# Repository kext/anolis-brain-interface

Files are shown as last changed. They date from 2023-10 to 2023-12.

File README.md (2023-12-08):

# Anolis Brain Interface

This repository contains the hardware and software files for the Anolis Brain Interface.

## PCB

The source and production files for the flexible PCB are in the [`pcb`](pcb) directory.
See the [Readme there](pcb/README.md) for instructions to setup your work environment.

## Firmware

The firmware for the brain interface and the dongle is in the [`firmware`](firmware) directory.
There you can find more information how to compile, flash and run the firmware on your device.

## Licence

The source code and PCB design files are dual licenced under the [MIT](LICENCE-MIT) and [Apache 2.0](LICENCE-APACHE) licences.

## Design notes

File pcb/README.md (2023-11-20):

# Anolis Brain Interface PCB

## Setup

To work on the project files you need the KiCad EDA software in version 7.

KiCad can be downloaded from the [KiCad website](https://www.kicad.org/).
Download the version for your operating system and follow the instructions.

## Releases

Released versions can be found in the [`releases`](releases) directory.

## Changelog

All notable changes to the PCB should be listed below.

### [0.1.0] - 2023-11-20
- First version

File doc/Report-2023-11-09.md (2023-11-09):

2023-11-09

# Anolis Brain Interface Report

## Concept

The Anolis Brain Interface consists of a flexible PCB to be mounted on the back of a lizard of the species *Anolis carolinensis*.
It measures brain activity of the animal and transmits the data in real time to a connected PC via Bluetooth.

## What has been done so far

### PCB

We have created a draft for a PCB for use with LiPo batteries.
It features a segmented design for increased flexibility.
It is still a bit big however.

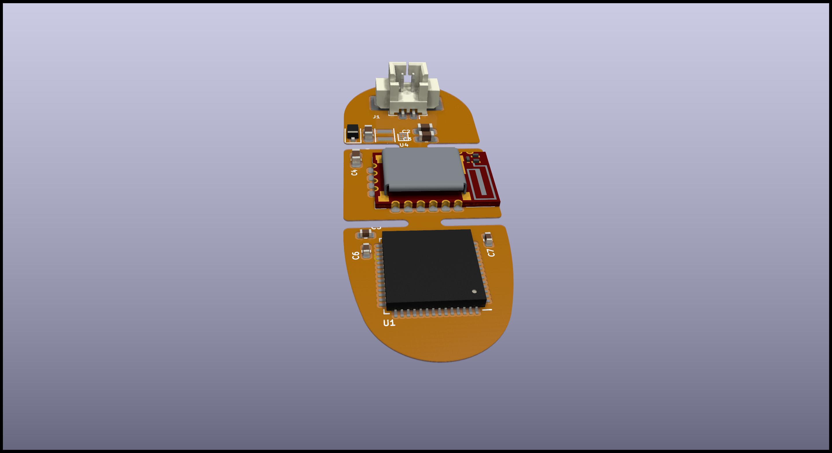
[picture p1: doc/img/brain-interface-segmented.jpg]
Segmented PCB

*Segmented PCB Draft*

After better estimation of the power requirements we will most likely change the design to use coin cell batteries instead.

We might also get rid of the segments to reduce the size further.

The brain interface is equipped with an analogue frontend in form of the Intan RHD2216 electrophysiological amplifier.
It also features the Würth Electronic Setebos-I Bluetooth module.
It contains a Bluetooth antenna and circuitry as well as the Nordic Semiconductor nRF52840 SoC which consists of a Bluetooth radio module and an ARM Cortex-M4F processor with 64MHz, 1MB flash memory and 256kB RAM.

### Software

A prototype of the software is complete by now.
It consists of three different parts.

The main software runs on the brain interface PCB.
It measures the electrophysiological signals with the Intan RHD2216 chip via SPI.
Then the collected data is transmitted in real time via a Bluetooth connection to a USB dongle.

The USB dongle runs a firmware which scans for and connects to the brain interface.
After a successful connection has been established it receives the data and transfers it via USB to the PC.

On the PC runs a frontend software in a web browser that connects to the dongle using the WebUSB API.
It collects the data and displays it in real time in the browser window.
It also saves the data for later conversion and analysis.

The software on the brain interface and the dongle are developed in the Rust language using the open-source Embassy framework.
The Embassy framework offers a high level abstraction over all the functionality of the nRF52840 SoC and makes it easy to implement concurrent tasks like reading the data from the analogue-to-digital converter while simultaneously sending data over the Bluetooth radio.

The frontend is written in Javascript using the Vue.js framework for the graphical user interface.

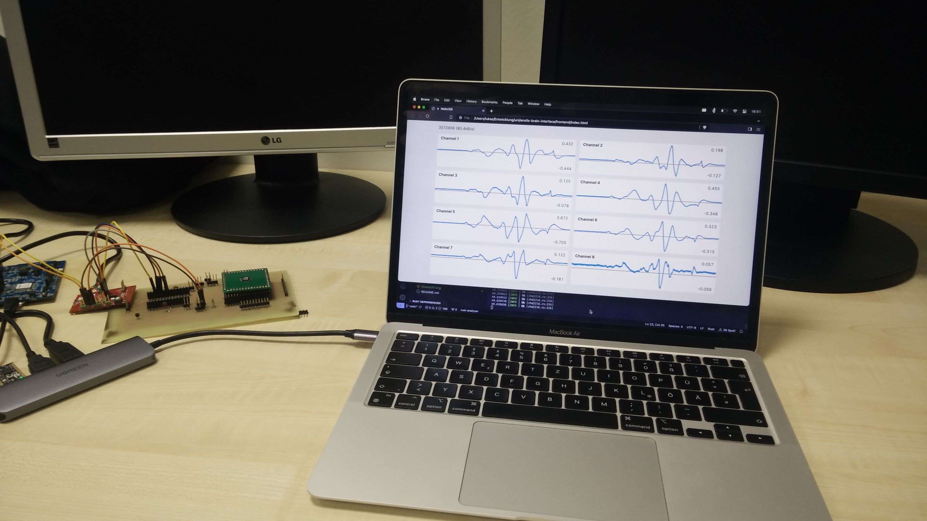
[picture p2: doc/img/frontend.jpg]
Frontend running on a laptop

*Frontend running on a laptop*

During development small improvements to the Embassy framework have been found and sent to the Embassy maintainers.
Those fixes are now upstreamed in the open-source project for the benefit of the community.

## Next steps

The biggest remaining challenge is the power supply for the system.
In the following days we will make several measurements of the power consumption of the brain interface and investigate how the sample rate and also the radio transmit power influence the power consumption.

Depending on the results of the power study we will finalize the PCB design for either a coin cell battery or a LiPo battery.
We will choose the lightest battery system that is still able to power the brain interface.

After that the software will be finalized, fixing eventual bugs and doing more testing.

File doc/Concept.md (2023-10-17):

# Concept

This project aims to build a device that is able to measure the bioelectric potential in the brains of Anolis lizards.
The device should be attached to the lizard and impact it as little as possible.

The data should be sampled at a decently high rate on multiple channels and then both be saved for later analysis and also displayed in realtime.

The realtime display is achieved by sending the data via Bluetooth to a connected PC.
Depending on the sample rate and the number of channels this is either all of the data or a reduced form.

In case only a reduced form can be sent in realtime, the data storage has to happen on the device itself.
A micro SD card would be the obvious choice for that.
Otherwise the data can just be recorded on the PC.

## Components

### Analogue Frontend

The analogue frontend is implemented with the Intan RHD2216 ADC.
It has 16 analogue differential inputs and an SPI connection to retrieve the data.

Depending on the configuration the RHD2216 draws between about 1mA to 15mA from a 3.3V power supply.

### Bluetooth Interface

The Bluetooth connectivity will be realized with the nRF52840 SoC by Nordic Semiconductor.
The SoC is powered by a 64MHz Arm Cortex M4F processor, which will not only handle the Bluetooth connection but will also run all the application code.

The highest contributor to power consumption is the Bluetooth radio.
Depending on the usage pattern the whole module should draw no more than about 20mA from the 3.3V supply while continuously transmitting data.

One of the smallest modules containing the nRF52840 is the Setebos-I by Würth Electronic.
It already contains the antenna circuit and the CPU.

For programming, a development kit with an SWD debugger is needed to flash the program onto the SoC.
The obvious choice here is the nRF52840-DK by Nordic Semiconductor.

To connect the module to a PC a Bluetooth dongle is needed.
A good choice will most likely be the nRF52840-Dongle by Nordic Semiconductor.
It uses the same nRF52840 SoC and thus supports the same level of Bluetooth communication including the new 2M PHY for higher data rate introduced in Bluetooth version 5.

### Data Storage

Data storage will happen on a micro SD card if the data rate is too high for realtime transmission.
In addition to the faster SD mode it can also be used via SPI which allows it to be connected directly to the processor.

If a micro SD card is required it will be the biggest consumer of power with peaks in excess of 100mA.
The power supply must therefore be able to handle this current and should be able to supply at least 300mA to leave enough capacity for the other components.

The micro SD card needs to be inserted into a socket.
The socket should be as small as possible and use up as little space on the board as possible.
A good choice will be the Molex socket 47571-0001.
It leaves enough clearance under the card that it can overlap other components.

### Power Supply

The system must be powered by batteries to enable a wireless operation.
Popular choices here are either rechargeable LiPo batteries often found in small model toys or Zinc-Air primary cells which have among the highest energy densities by both mass and weight, often found in hearing aids.

When using LiPo batteries, a charging circuit and voltage converter is required to keep the voltage at a steady 3.3V and to charge the battery.

For use with Zinc-Air coin cells a boost converter is needed to step up the 1.45V up to the required 3.3V.
A good choice might be the TPS610994 by Texas Instruments.
It has a very low quiescent current and can use the battery until it has dropped to 0.7V.
An even better choice might be the TPS61299 but it is not widely available yet.

## Requirements

A number of requirements have to be specified to properly dimension the project.

### Channel Count

The channel count not only influences the data rate but also dictates how much board space is needed for the connectors and the electrodes.
The maximum channel count possible with the RHD2216 is 16 channels.

Also important is if the channels should share a common reference or if each channel is using the full differential input.

### Sample Rate

The sample rate has the biggest influence on the overall data rate.
If the data rate is too high the micro SD card for data storage can not be omitted from the system.
If it is lower the complete data can be transferred via Bluetooth to be recorded directly on the PC.

### Bit Depth

The RHD2216 by default has a bit depth of 16 bits per sample.
This has a lower overall impact, but reducing the bit depth by either limiting the input range by removing high order bits or by reducing the resolution by removing low order bits can significantly decrease the data rate.
Another possibility would be using dynamic range compression, i.e. companding the signal by applying a non-linear function before reduction.

### Operating Time

The required operating time dictates how many batteries are required and how big those have to be.
A longer operating time means bigger or more batteries and thus heavier weight and larger dimensions of the overall system.

### Electrodes

The type, shape, number and dimensions of the electrodes must be known.
The electrodes influence significantly how the system has to be designed and mounted.
Possible configurations include mounting the PCB either on the head or on the back of the lizard.

## Part List

The following parts are needed for the development.

Part               | Supplier | Order Number
-------------------|----------|---------------------
nRF52840-DK        | Mouser   | [949-NRF52840-DK](https://www.mouser.de/c/?q=949-NRF52840-DK)
nRF52840-Dongle    | Mouser   | [949-NRF52840-DONGLE](https://www.mouser.de/c/?q=949-NRF52840-DONGLE)
Setebos-I          | Farnell  | [3868806](https://de.farnell.com/search?st=3868806)
TPS610994YFFR      | Mouser   | [595-TPS610994YFFR](https://www.mouser.de/c/?q=595-TPS610994YFFR)
VLS201610CX-2R2M-1 | Mouser   | [810-VLS201610CX2R2M1](https://www.mouser.de/c/?q=810-VLS201610CX2R2M1)
47571-0001         | Mouser   | [538-47571-0001](https://www.mouser.de/c/?q=538-47571-0001)

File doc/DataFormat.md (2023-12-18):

# Storage Data Format

The data file contains all data packets received by the brain interface together with the time the packet was received.
The data file includes all the data packets with a header one after the other.

Each stored packet has the following format:

Field | Byte Offset | Byte Size | Data Type | Description
------|-------------|-----------|-----------|------------
Signature | 0 | 4 | `u32` | The fixed value 0x55daba to identify the file.
Length | 4 | 4 | `u32` | Length of the stored packet in bytes including this header.
Time | 8 | 8 | `u64` | Time this packet was received as number of milliseconds since `1970-01-01T00:00Z`.
Packet Number | 16 | 1 | `u8` | A counter to detect missing packets. Wraps to 0 after 255.
Channel Count | 17 | 1 | `u8` | Number of channels in this packet.
Samples | 18 | Variable | `[u16]` | All samples of the packet as 16 bit integers.

All integer types are in little endian byte order, i.e. least significant byte first.

The samples are stored interleaved with one sample for each channel until there are no more samples.

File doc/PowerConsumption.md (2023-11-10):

# Power Consumption

The power consumption of the system depends strongly on the data rate and the transmit power.

We measured the current for different combinations of sample rate and transmit power using the voltage drop over a 680mΩ resistor.
The voltage drop has been amplified by a factor of 100 with an INA180 current sense amplifier and then sampled with 1.5MHz with a logic analyser.
This makes it possible to see the current consumption during different activities.
It is possible to clearly see the current during radio transmit, radio receive and idle.

The traces have then been analysed for minimum, mean and peak current over 500ms windows.

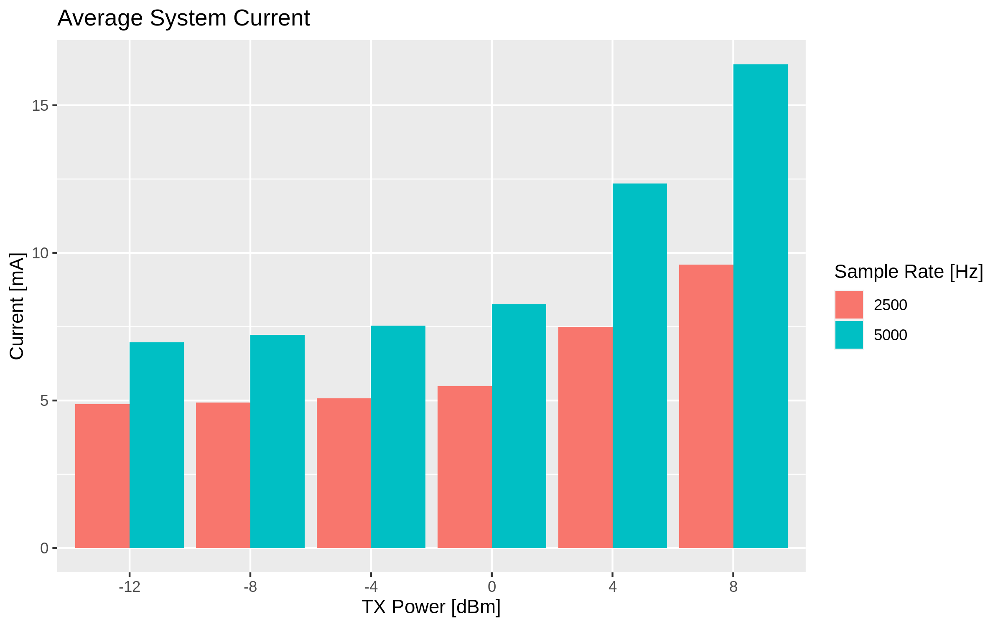
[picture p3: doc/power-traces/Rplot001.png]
Average System Current


We can clearly see that the average current increases significantly when raising the transmit power over 0dBm.
This results in increased range but that is probably not needed.
Below 0dBm the savings for decreasing transmit power are a lot less severe.

What can also be seen is that the sample rate has a big influence on overall power consumption.
A lower sample rate results in a lower data rate which reduces radio time spent transmitting data packets.

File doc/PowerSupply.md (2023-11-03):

# Power Supply

As it turns out the power supply might be one of the biggest challenges in the project.

After discarding the micro SD card from the design, the biggest impact on power is the sample rate.
The sample rate simultaneously affects the data rate that has to be transmitted over Bluetooth as well as the power consumption of the AD converter.

The Bluetooth radio needs up to 20mA during transmissions, thus reducing air time is a way to reduce the average current.
Reducing the data rate directly reduces air time.
By including a large enough capacitance on the board it should be possible to smooth out the peak current enough to prevent large voltage drops from the battery.

While zinc-air batteries have very high power densities and low masses, they also have very limited current capabilities.
Smaller zinc-air batteries can supply only about 10mA of current while dropping to a voltage of about 1V.
At this voltage a current of more than 50mA would be needed though.

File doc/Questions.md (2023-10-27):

# Questions

## For the Biologists

### How many electrodes are needed?

This influences how many channels are needed on the PCB.

**Answer:** As many as possible.
Let's start with 8 channels, i.e. 9 electrodes.

### What type of electrodes will be used?

How big are they?
How are they attached?
How long and thick are the wires?

**Answer:** Wire diameter 75µm.

[FE6215 Stainless Steel AISI 316L Insulated Wire](https://www.advent-rm.com/en-GB/Search?SearchTerm=FE6215)

We can not use the Neuropixels without significantly changing the system.
Also their power consumption and data rate is way too high.

### What are the frequencies of the signals?

This determines the sample rate and cut off frequency used for the ADC.

**Answer:** Maybe 2kHz is enough.
We will go as high as possible with 8 channels.
5kHz should be doable.

### How and where should the board be attached?

The board could be attached either on the head or on the back of the lizard.
Will it be glued or strapped to the lizard?

We could include slits at the sides of the PCB to attach a strapping belt.

**Answer:** Probably glueing.

*Note:* Include slits between the components to allow for more flexing of the board.

### How long will the experiments last?

This determines how much battery capacity is needed.

**Answer:** Saving weight is paramount.
We go with the lightest battery that can still power the system.

### Which species of lizard will be examined?

How big are they?
What is their weight?
How much can they carry without being impacted?

**Answer:** Anolis Carolinensis.
About 6-7g.
They can carry maybe 3-4g.

## For us

### Which battery type to use?

We could use either lithium button cells, zinc-air button cells or LiPo rechargeable batteries.

**Answer:** We should use the lightest battery that can supply the system.

### Can a zinc-air battery supply the needed current?

When using a micro SD card, the power supply needs to be able to supply peak currents of 200mA.
With the lower voltage of the zinc-air button cell of 1.45V vs the 3.3V operating voltage this current increases to about 450mA.

We should conduct an experiment where we discharge a number of coin cells with different currents both pulsed and continuously.
This also can show us the expected operation time for each type of battery.

**Answer:** Without the micro SD card this should be possible.
With the micro SD card the current is too large.

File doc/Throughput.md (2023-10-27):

# Throughput

Theoretical throughput at 2M with Data Length Extension and a 50ms connection interval: 1366kbit/s.

If we can keep our data rate below this threshold the SD card is not necessary.
Since it is by far the largest consumer of energy this would make the system a lot smaller and lighter.

## Data Rates

The data rate of the system depends on the sample rate, the channel count and the bits per sample.

Channels | Sample Rate | Bit Depth | Data Rate  | Ok?
---------|-------------|-----------|------------|------
16       | 10kHz       | 16bit     | 2560kbit/s | No
10       | 10kHz       | 16bit     | 1600kbit/s | No
8        | 10kHz       | 16bit     | 1280kbit/s | Maybe
10       | 10kHz       | 10bit     | 1000kbit/s | Yes
10       | 5kHz        | 16bit     | 800kbit/s  | Yes

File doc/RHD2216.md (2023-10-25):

# RHD2216

[Product Page](https://intantech.com/products_RHD2000.html) |
[Data Sheet](https://www.intantech.com/files/Intan_RHD2000_series_datasheet.pdf)

The RHD2216 is a low-power electrophysiology signal acquisition chip containing 16 differential input channels each with a low-noise amplifier.
It also contains a multiplexed ADC to digitise the channels and an SPI interface for communication with an MCU.

## Data Readout

To ensure a steady sampling rate the ADC has to be fed commands at a steady pace.
One command has to be sent for every channel that should be read followed by a few dummy commands to give enough time for the results.

The firmware ensures this by programming `TIMER1` to generate the command pacing.
The overflow event is connected to the start transaction task of the `SPI3` module using the PPI.
Thus every time the timer overflows it starts a new SPI transaction.
The `SPI3` module is used because it is the only SPI module with support for generating the chip select signal.
When a transaction starts the SPI module automatically lowers the CS line, transfers two bytes with the DMA, raises the CS line again and generates the transaction complete event.
The DMA is set to list mode which ensures the DMA pointer is automatically increased to the next command when the transaction has been started.

The `TIMER2` module is set to counter mode and its count task is connected to the transaction completion event of the SPI module.
When the counter reaches a predefined value it is reset and triggers an interrupt.

All of this happens completely without any CPU interaction.
The CPU only gets involved when the counter interrupt is executed.
In this interrupt the CPU has to rewind the TX buffer, swap the RX buffer and then pass on the data to the main task.

### SPI Buffers

The firmware reserves three buffers for the DMA.
One TX buffer and two RX buffers.
Each buffer is large enough to contain 11ms worth of commands.
Every 10ms the counter interrupt is triggered.

The TX buffer contains the commands that have to be sent to the ADC.
During the first iteration this contains all the commands needed to calibrate and start the ADC.
When the first interrupt happens this gets overwritten with the commands for the data readout.

The RX buffers get filled with the results of the ADC.
Every time the interrupt happens it swaps the DMA pointer to the other RX buffer and then copies the sample data over to the main task.
Not every value in the RX buffer is sample data.
The responses to the dummy commands get filtered out during the copy process.

As stated every buffer is large enough to hold 11ms worth of data but the interrupt is triggered every 10ms.
This means all buffers have a 1ms overflow window.
When the buffers reach the 10ms mark there is a time window of 1ms where additional data can accumulate before the buffers have to be swapped.
This is necessary because the command pacing is very fast and the interrupt can be delayed by up to 250µs by the Bluetooth module.
During this time the data gets written to the old buffer's overflow area.
After the buffer has been swapped the data from the overflow area is copied to the start of the new buffer.

Swapping the buffer itself means changing the value of the DMA pointer while the SPI module is running.
Great care has to be taken to ensure that the pointer does not get corrupted by a data race.
This is managed by the `adjust_pointer` function.
It is written in inline assembler and uses the `LDREX` and `STREX` ARM instructions for exclusive loads and stores.
First the DMA pointer is loaded with the `LDREX` instruction setting the exclusive bit for the CPU.
In case of a context switch by an interrupt this exclusive bit is cleared and the following `STREX` instruction fails.
In that case the procedure is retried from the beginning.
After the load `TIMER1` is checked for a safe value.
If it is currently too close to before or after overflowing the procedure is restarted as well.
This ensures that the DMA pointer access is retried until it is safe to do so.

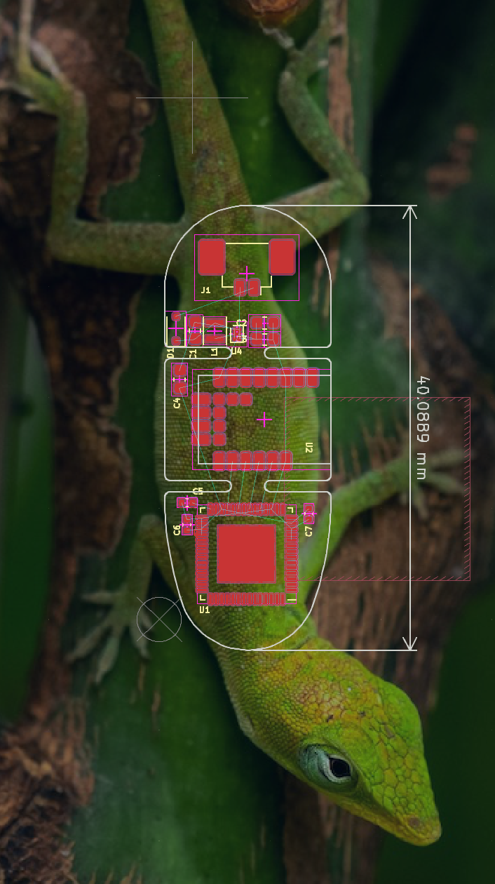
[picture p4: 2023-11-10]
doc/img/board-dimensions.png

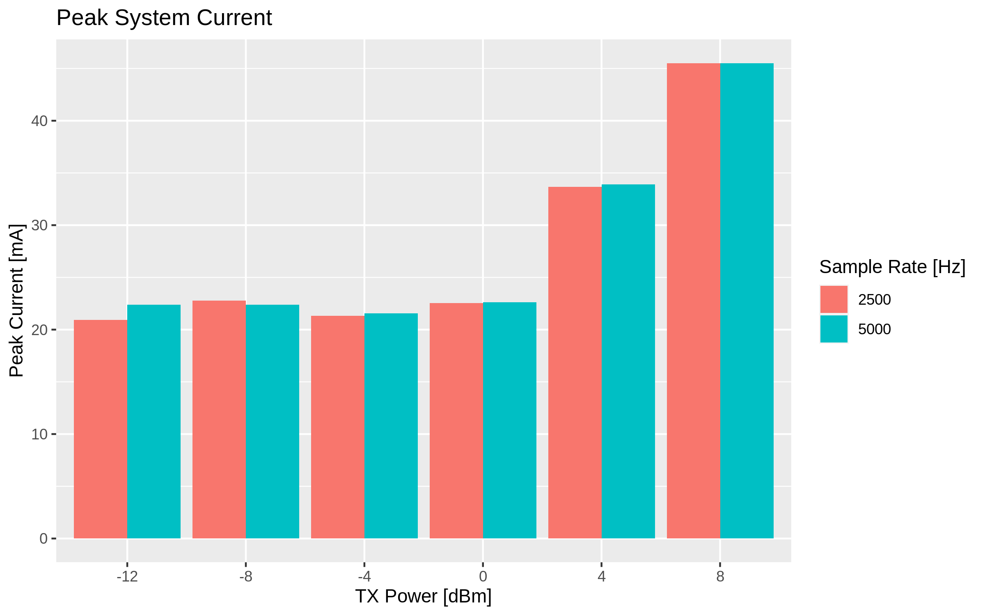
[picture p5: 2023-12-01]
doc/power-traces/Rplot002.png

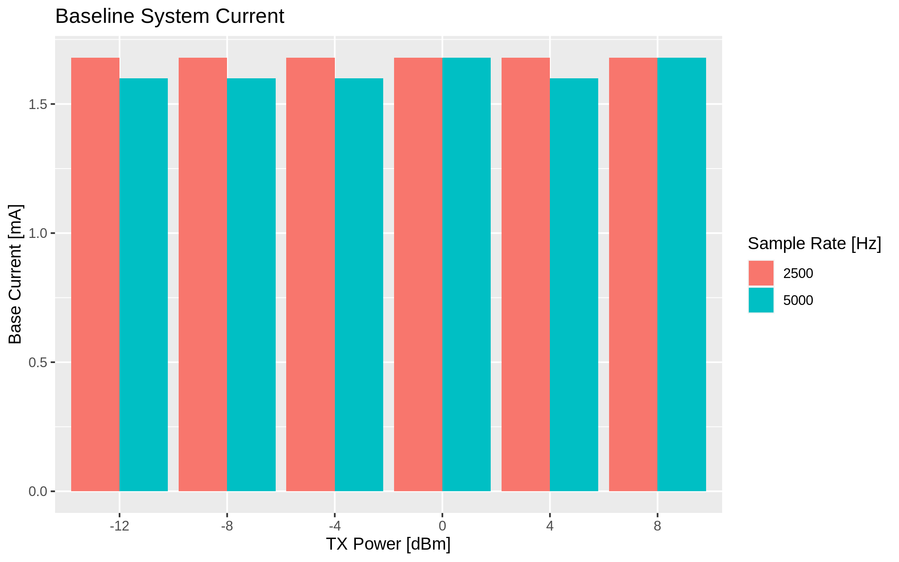
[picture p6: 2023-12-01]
doc/power-traces/Rplot003.png

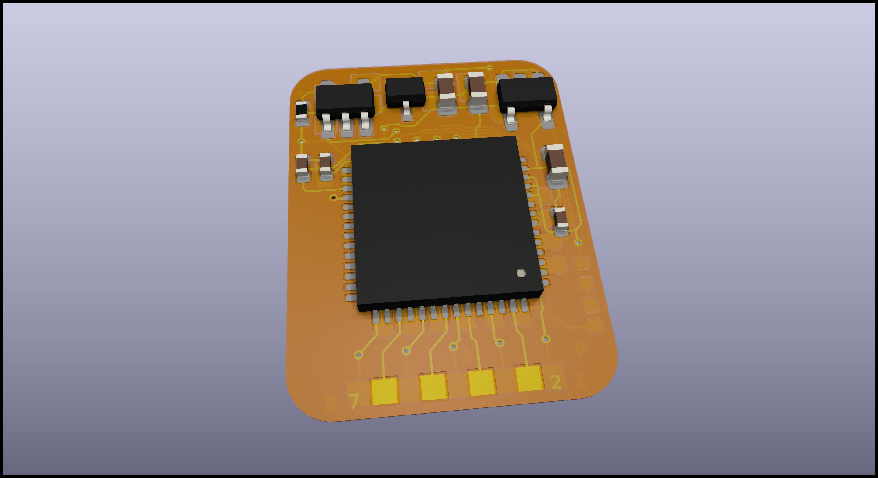
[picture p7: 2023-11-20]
pcb/releases/v0.1.0/anolis-brain-interface-bottom.jpg

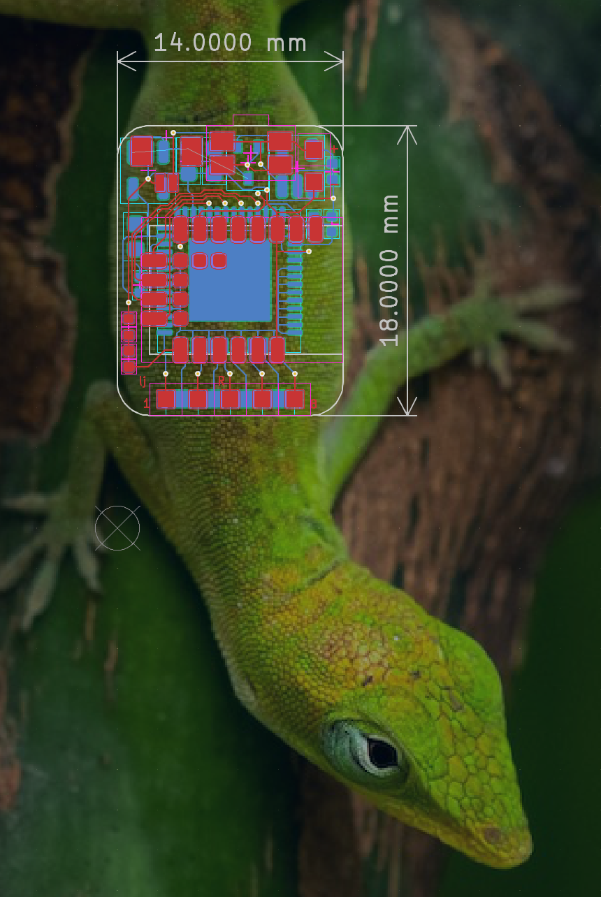
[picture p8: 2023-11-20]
pcb/releases/v0.1.0/anolis-brain-interface-dimensions.png

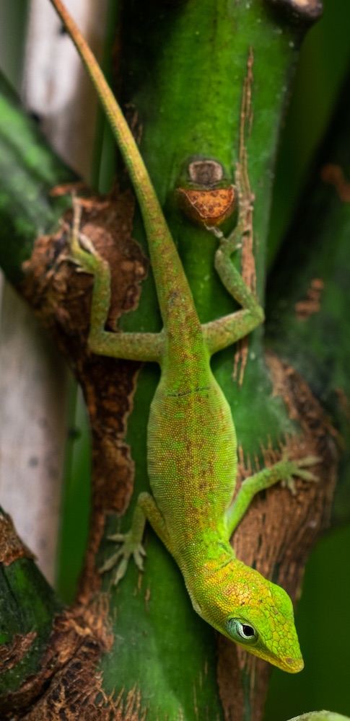
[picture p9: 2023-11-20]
pcb/anolis.jpg

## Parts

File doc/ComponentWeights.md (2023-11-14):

# Component Weights

Component          | Weight
-------------------|-------
Setebos-I          | 0.30g
RHD2216            | 0.17g
PCB (old)          | 0.33g
LR1130 Coin Cell   | 1.14g
Battery 150mAh     | 3.76g
Battery 100mAh     | 3.57g
Battery 80mAh      | 2.62g
Long Battery 80mAh | 2.14g
Battery 40mAh      | 1.03g

When using the 40mAh battery it should be possible to keep the system weight at 2g not including the electrodes.

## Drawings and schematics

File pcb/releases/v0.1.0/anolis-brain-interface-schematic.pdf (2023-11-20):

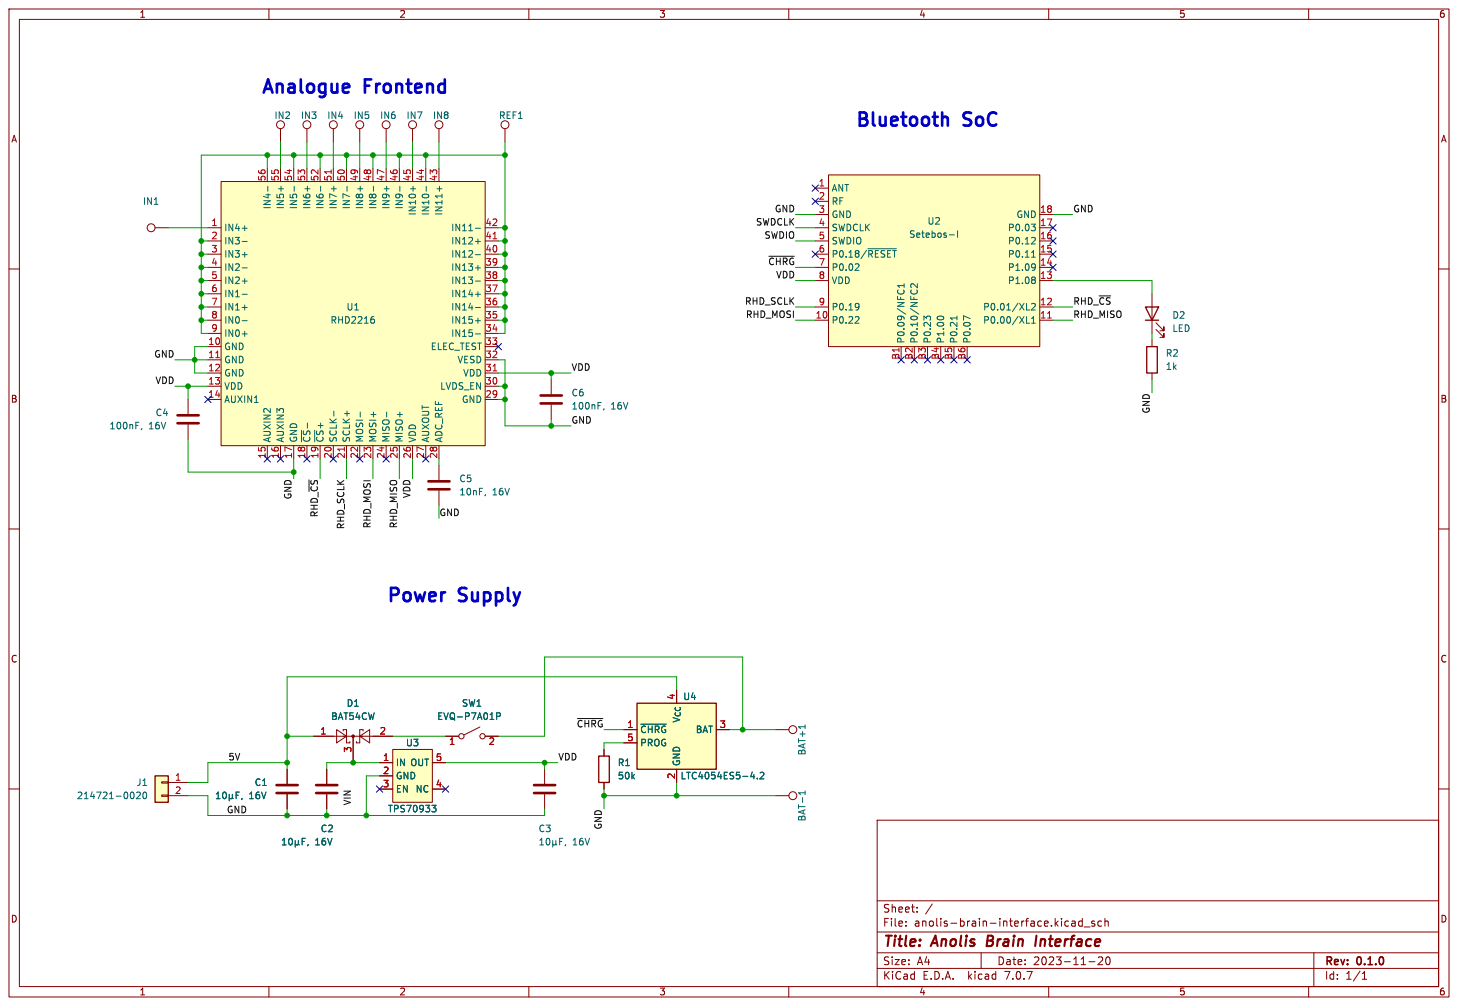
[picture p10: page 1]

File: anolis-brain-interface.kicad_sch Sheet: / C5

Id: 1/1 Title: Anolis Brain Interface

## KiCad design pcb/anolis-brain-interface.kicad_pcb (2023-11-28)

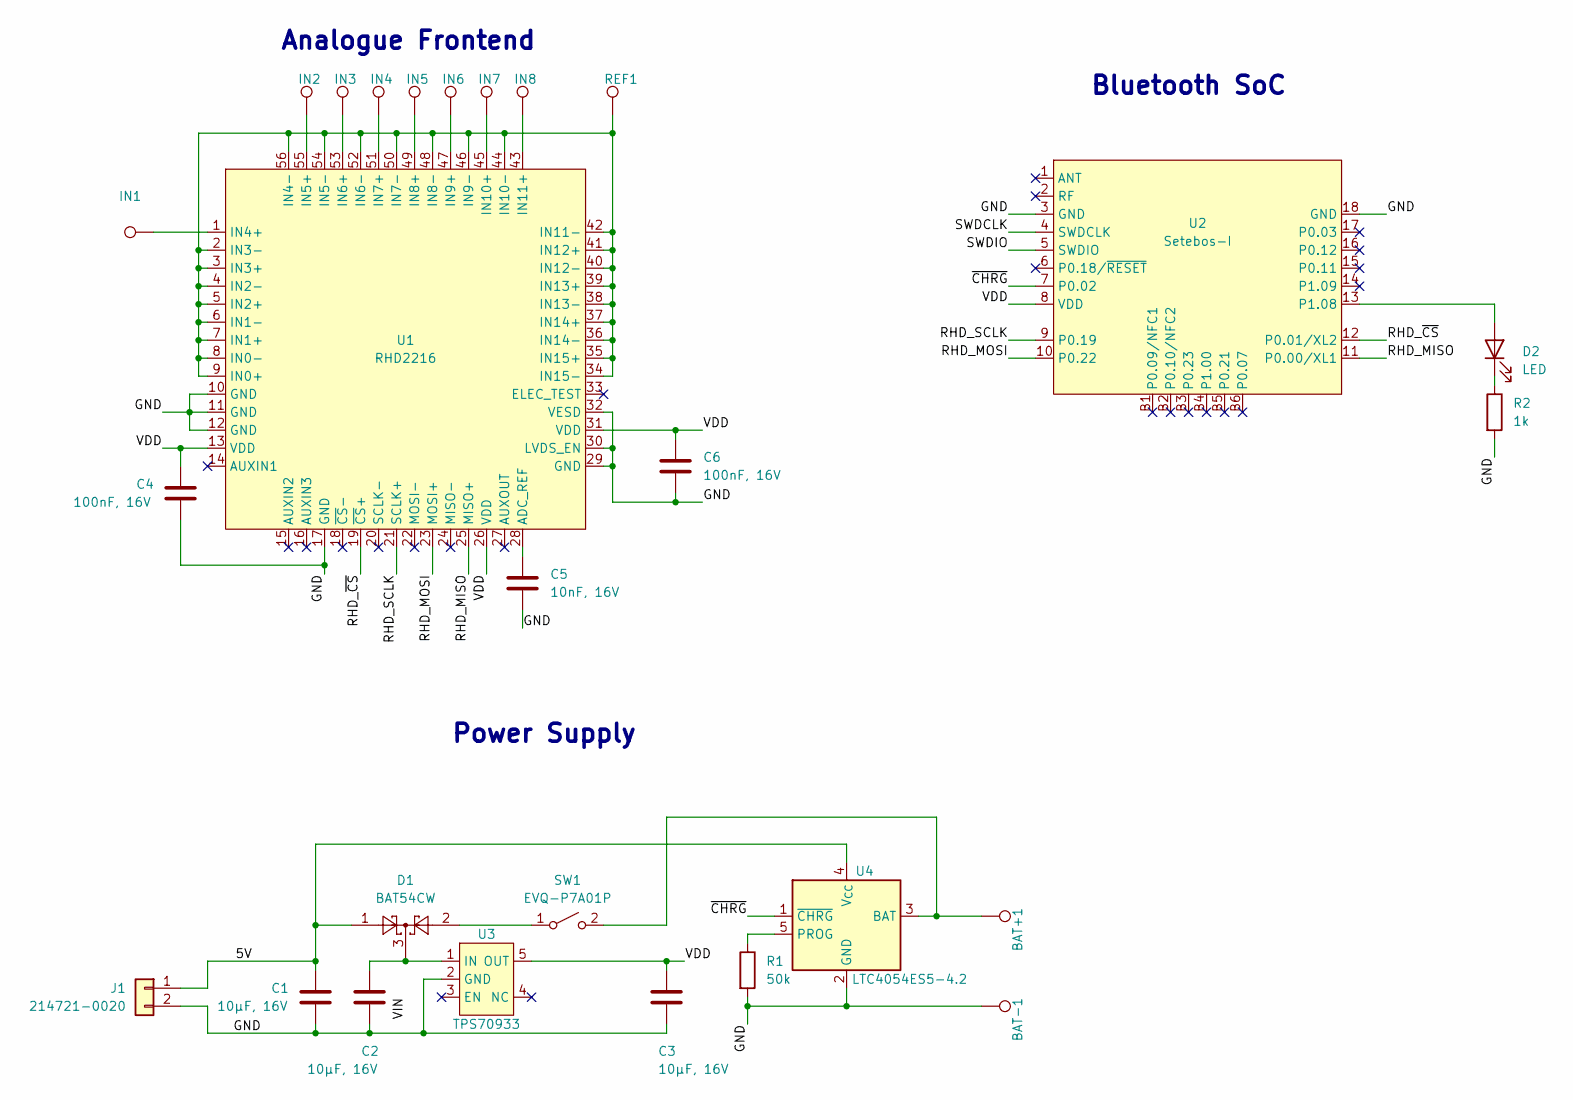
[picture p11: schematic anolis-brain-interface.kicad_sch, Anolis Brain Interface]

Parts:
BAT+1: TestPoint; TestPoint_Pad_1.0x1.0mm
BAT-1: TestPoint; TestPoint_Pad_1.0x1.0mm
C1, C2, C3: 10µF, 16V; C_0603_1608Metric
C4, C6: 100nF, 16V; C_0402_1005Metric
C5: 10nF, 16V; C_0402_1005Metric
D1: BAT54CW; SOT-323_SC-70
D2: LED; LED_0402_1005Metric
IN1, IN2, IN3, IN4, IN5, IN6, IN7, IN8: TestPoint; TestPoint_Pad_1.0x1.0mm
J1: 214721-0020
R1: 50k; R_0402_1005Metric
R2: 1k; R_0402_1005Metric
REF1: TestPoint; TestPoint_Pad_1.0x1.0mm
SW1: EVQ-P7A01P; SW_SPST_EVQP7A
U1: RHD2216; QFN-56-EP
U2: Setebos-I; setebos-no-drc
U3: TPS70933; TSOT-23-5
U4: LTC4054ES5-4.2; TSOT-23-5

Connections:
/5V: C1.1, D1.1, J1.1, U4.4 (V_{CC})
/GND: BAT-1.1, C1.2, C2.2, C3.2, C4.2, C5.2, C6.2, J1.2, R1.2, R2.2, U1.10 (GND), U1.11 (GND), U1.12 (GND), U1.17 (GND), U1.29 (GND), U1.30 (LVDS_EN), U1.32 (VESD), U2.3 (GND), U2.18 (GND), U3.2 (GND), U4.2 (GND)
/RHD_MISO: U1.25 (MISO+), U2.11 (P0.00/XL1)
/RHD_MOSI: U1.23 (MOSI+), U2.10 (P0.22)
/RHD_SCLK: U1.21 (SCLK+), U2.9 (P0.19)
/RHD_~CS: U1.19 (~CS+), U2.12 (P0.01/XL2)
/SWDCLK: U2.4 (SWDCLK)
/SWDIO: U2.5 (SWDIO)
/VDD: C3.1, C4.1, C6.1, U1.13 (VDD), U1.26 (VDD), U1.31 (VDD), U2.8 (VDD), U3.5 (OUT)
/~CHRG: U2.7 (P0.02), U4.1 (~CHRG)
unnamed: D2.2 (A), U2.13 (P1.08)
unnamed: D2.1 (K), R2.1
unnamed: D1.2, SW1.1 (A)
unnamed: BAT+1.1, SW1.2 (B), U4.3 (BAT)
unnamed: C5.1, U1.28 (ADC_REF)
unnamed: REF1.1, U1.2 (IN3-), U1.3 (IN3+), U1.4 (IN2-), U1.5 (IN2+), U1.6 (IN1-), U1.7 (IN1+), U1.8 (IN0-), U1.9 (IN0+), U1.34 (IN15-), U1.35 (IN15+), U1.36 (IN14-), U1.37 (IN14+), U1.38 (IN13-), U1.39 (IN13+), U1.40 (IN12-), U1.41 (IN12+), U1.42 (IN11-), U1.44 (IN10-), U1.46 (IN9-), U1.48 (IN8-), U1.50 (IN7-), U1.52 (IN6-), U1.54 (IN5-), U1.56 (IN4-)
unnamed: IN1.1, U1.1 (IN4+)
unnamed: IN2.1, U1.55 (IN5+)
unnamed: IN3.1, U1.53 (IN6+)
unnamed: IN4.1, U1.51 (IN7+)
unnamed: IN5.1, U1.49 (IN8+)
unnamed: IN6.1, U1.47 (IN9+)
unnamed: IN7.1, U1.45 (IN10+)
unnamed: IN8.1, U1.43 (IN11+)
unnamed: C2.1, D1.3, U3.1 (IN)
unnamed: R1.1, U4.5 (PROG)

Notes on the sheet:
Power Supply
Analogue Frontend
Bluetooth SoC

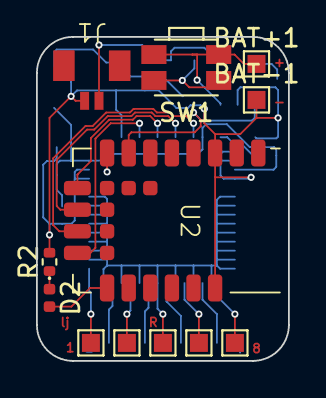
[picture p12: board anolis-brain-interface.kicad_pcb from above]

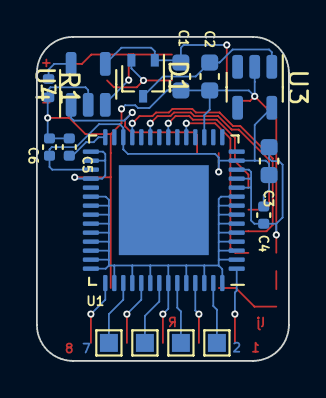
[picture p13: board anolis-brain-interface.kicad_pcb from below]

Board: 2 copper layers, 14.0 x 18.0 mm, 27 parts (15 on the bottom side), 24 nets.

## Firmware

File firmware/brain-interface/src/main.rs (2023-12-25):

//! Firmware for the Anolis Brain Interface

#![no_std]
#![no_main]
#![feature(type_alias_impl_trait)]

extern crate alloc;

use core::{cell::RefCell, ops::BitAnd};

use data_channel::{BoxPacket, L2capError};
use defmt::{info, unwrap, warn};
use embassy_executor::Spawner;
use embassy_futures::join::join;
use embassy_nrf::{
    bind_interrupts,
    gpio::{AnyPin, Input, Level, Output, OutputDrive, Pull},
    interrupt, peripherals,
    uarte::{self, UarteTx},
};
use embassy_time::Timer;
use embedded_alloc::Heap;
use nrf_softdevice::{
    ble::{
        l2cap::{self, L2cap, Packet, RxError},
        peripheral::{self, ConnectableAdvertisement},
        Phy, TxPower,
    },
    raw, Softdevice,
};

// global logger
use defmt_rtt as _;
// time driver
use embassy_nrf as _;
use panic_probe as _;

mod rhd2216;
use rhd2216::RHD2216;

/// Use the embedded alloc heap to enable [`Vec`](alloc::vec::Vec) and [`BoxPacket`].
#[global_allocator]
static HEAP: Heap = Heap::empty();

bind_interrupts!(struct Irqs {
    TIMER2 => rhd2216::InterruptHandler;
    UARTE1 => uarte::InterruptHandler<peripherals::UARTE1>;
});

/// The Softdevice task. Must be started after enabling the Softdevice.
#[embassy_executor::task]
async fn softdevice_task(sd: &'static Softdevice) -> ! {
    sd.run().await
}

#[embassy_executor::task]
async fn blink_task(led_pin: AnyPin, chrg_pin: AnyPin) -> ! {
    let mut led = Output::new(led_pin, Level::Low, OutputDrive::Standard);
    let chrg_status = Input::new(chrg_pin, Pull::Up);
    loop {
        for i in 0..4 {
            led.set_level(Level::from(i.bitand(1) == 0 || chrg_status.is_high()));
            Timer::after_millis(500).await;
        }
    }
}

/// Advertisement data for the device.
/// Contains the UUID of the brain interface service so the dongle knows to which device to connect.
#[rustfmt::skip]
const ADVERTISEMENT_DATA: &[u8] = &[
    // Flags
    2, 1, raw::BLE_GAP_ADV_FLAGS_LE_ONLY_GENERAL_DISC_MODE as u8,
    // Complete List of 128-bit Service Class UUIDs
    // edb74b42-8347-4285-a102-86f0b64c533c
    17, 7,
    0x3c, 0x53, 0x4c, 0xb6, 0xf0, 0x86, 0x02, 0xa1,
    0x85, 0x42, 0x47, 0x83, 0x42, 0x4b, 0xb7, 0xed,
];

/// Get the [`ConnectableAdvertisement`] for this device.
pub fn advertisement() -> ConnectableAdvertisement<'static> {
    ConnectableAdvertisement::ScannableUndirected {
        adv_data: ADVERTISEMENT_DATA,
        scan_data: &[],
    }
}

/// Alias for the packet type to have one place to change the size.
type MyPacket = BoxPacket<2048>;

/// Shared state between the receiver and sender task.
#[derive(defmt::Format)]
struct State {
    should_stop: bool,
}

/// Start the RHD and keep sending data packets over the L2CAP channel.
async fn send_rhd_data(
    rhd: &mut RHD2216<'_>,
    channel: &l2cap::Channel<MyPacket>,
    state: &RefCell<State>,
) -> Result<(), L2capError<MyPacket>> {
    info!("Starting");
    let mut rhd = rhd.start();
    loop {
        if state.borrow().should_stop {
            return Ok(());
        }
        let d = rhd.read().await;
        let mut packet = MyPacket::new().ok_or(RxError::AllocateFailed)?;
        assert!(MyPacket::MTU / 2 > d.frames.len());
        packet.append(&[(d.sequence_number & 255) as u8, d.channels as u8]);
        for v in &d.frames {
            packet.append(&v.to_le_bytes());
        }
        channel.try_tx(packet).or_else(|e| {
            if let l2cap::TxError::TxQueueFull(_) = e {
                warn!("Packet lost");
                Ok(())
            } else {
                Err(e)
            }
        })?;
    }
}

/// Receive commands and interpret them.
async fn receive_commands(channel: &l2cap::Channel<MyPacket>, state: &RefCell<State>) -> () {
    if let Ok(_) = channel.rx().await {
        state.borrow_mut().should_stop = true;
    }
}

/// The main task.
#[embassy_executor::main]
async fn main(spawner: Spawner) {
    info!("Start");

    // Initialise allocator
    {
        use core::mem::MaybeUninit;
        const HEAP_SIZE: usize = 1024 * 128;
        static mut HEAP_MEM: [MaybeUninit<u8>; HEAP_SIZE] = [MaybeUninit::uninit(); HEAP_SIZE];
        unsafe { HEAP.init(HEAP_MEM.as_ptr() as usize, HEAP_SIZE) }
    }

    // First we get the peripherals access crate.
    let mut config = embassy_nrf::config::Config::default();
    config.gpiote_interrupt_priority = interrupt::Priority::P3;
    config.time_interrupt_priority = interrupt::Priority::P3;
    let p = embassy_nrf::init(config);

    let config = nrf_softdevice::Config {
        clock: Some(raw::nrf_clock_lf_cfg_t {
            source: raw::NRF_CLOCK_LF_SRC_SYNTH as u8,
            rc_ctiv: 0,
            rc_temp_ctiv: 0,
            accuracy: raw::NRF_CLOCK_LF_ACCURACY_500_PPM as u8,
        }),
        conn_gap: Some(raw::ble_gap_conn_cfg_t {
            conn_count: 1,
            event_length: 40,
        }),
        conn_gatt: Some(raw::ble_gatt_conn_cfg_t { att_mtu: 256 }),
        conn_gattc: Some(raw::ble_gattc_conn_cfg_t {
            write_cmd_tx_queue_size: 0,
        }),
        conn_gatts: Some(raw::ble_gatts_conn_cfg_t {
            hvn_tx_queue_size: 0,
        }),
        gatts_attr_tab_size: Some(raw::ble_gatts_cfg_attr_tab_size_t {
            attr_tab_size: 1024,
        }),
        gap_role_count: Some(raw::ble_gap_cfg_role_count_t {
            adv_set_count: 1,
            periph_role_count: 1,
            central_role_count: 1,
            central_sec_count: 0,
            _bitfield_1: raw::ble_gap_cfg_role_count_t::new_bitfield_1(0),
        }),
        gap_device_name: Some(raw::ble_gap_cfg_device_name_t {
            p_value: b"Brain Interface" as *const u8 as _,
            current_len: 15,
            max_len: 15,
            write_perm: raw::ble_gap_conn_sec_mode_t {
                _bitfield_1: raw::ble_gap_conn_sec_mode_t::new_bitfield_1(1, 1),
            },
            _bitfield_1: raw::ble_gap_cfg_device_name_t::new_bitfield_1(
                raw::BLE_GATTS_VLOC_STACK as u8,
            ),
        }),
        conn_l2cap: Some(raw::ble_l2cap_conn_cfg_t {
            ch_count: 1,
            rx_mps: 256,
            tx_mps: 256,
            rx_queue_size: 3,
            tx_queue_size: data_channel::QUEUE_SIZE,
        }),
        ..Default::default()
    };

    // Pin definitions
    let _b1: AnyPin = p.P0_09.into();
    let _b2: AnyPin = p.P0_10.into();
    let _b3: AnyPin = p.P0_23.into();
    let _b4: AnyPin = p.P1_00.into();
    let _b5: AnyPin = p.P0_21.into();
    let _b6: AnyPin = p.P0_07.into();

    let _chrg: AnyPin = p.P0_02.into();

    let _led: AnyPin = p.P1_08.into();

    let _rhd_cs: AnyPin = p.P0_01.into();
    let _rhd_clk: AnyPin = p.P0_19.into();
    let _rhd_mosi: AnyPin = p.P0_22.into();
    let _rhd_miso: AnyPin = p.P0_00.into();

    let sd = Softdevice::enable(&config);
    let l2cap = L2cap::init(sd);

    unwrap!(spawner.spawn(softdevice_task(sd)));
    unwrap!(spawner.spawn(blink_task(_led, _chrg)));

    // Enable UARTE, otherwise SPI3 will not work.
    let mut uart = UarteTx::new(p.UARTE1, Irqs, _b1, Default::default());
    let _ = uart.write(&[1, 2, 3]).await;

    let mut rhd = RHD2216::new(
        Irqs,
        p.SPI3,
        p.TIMER1,
        p.TIMER2,
        p.PPI_CH0.into(),
        p.PPI_CH1.into(),
        _rhd_cs,
        _rhd_clk,
        _rhd_mosi,
        _rhd_miso,
    );

    loop {
        info!("Waiting for connection");
        let config = peripheral::Config {
            tx_power: TxPower::Plus8dBm,
            secondary_phy: Phy::M2,
            interval: 160,
            ..Default::default()
        };

        if let Ok(connection) =
            peripheral::advertise_connectable(sd, advertisement(), &config).await
        {
            info!("advertising done! I have a connection.");
            let config = nrf_softdevice::ble::l2cap::Config { credits: 3 };
            let channel = l2cap.listen(&connection, &config, data_channel::PSM).await;
            if let Ok(channel) = channel {
                let state = RefCell::new(State { should_stop: false });
                let _result = join(
                    send_rhd_data(&mut rhd, &channel, &state),
                    receive_commands(&channel, &state),
                )
                .await;
                info!("{}", _result);
            }
        }
        Timer::after_millis(1000).await;
    }
}

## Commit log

2023-10-17 Started work on PCB.
    [anolis-brain-interface.kicad_pcb, anolis-brain-interface.kicad_sch]
2023-10-17 Added uSD socket.
    [anolis-brain-interface.kicad_pcb, anolis-brain-interface.kicad_sch]
2023-10-18 Added power supply.
    [anolis-brain-interface.kicad_pcb, anolis-brain-interface.kicad_sch]
2023-10-18 Added capacitors.
    [anolis-brain-interface.kicad_pcb, anolis-brain-interface.kicad_sch]
2023-10-18 Added attachment slits.
    [anolis-brain-interface.kicad_pcb]
2023-10-18 Changed board material to polyimide.
    [anolis-brain-interface.kicad_pcb]
2023-10-18 Added battery connector.
    [anolis-brain-interface.kicad_pcb, anolis-brain-interface.kicad_sch]
2023-10-19 Diode added.
    [anolis-brain-interface.kicad_pcb, anolis-brain-interface.kicad_sch]
2023-10-25 Don't forget the samples in the first overflow.
2023-10-30 Segmented draft.
    [anolis-brain-interface.kicad_pcb, anolis-brain-interface.kicad_sch]
2023-11-03 Power supply documentation.
2023-11-10 Measured power consumption.
    [data.csv]
2023-11-10 A picture of the estimated board dimensions.
2023-11-17 New PCB design.
    [anolis-brain-interface.kicad_pcb, anolis-brain-interface.kicad_sch]
2023-11-20 PCB done.
    [anolis-brain-interface.kicad_pcb, anolis-brain-interface.kicad_sch]
2023-11-20 Improved routing.
    [anolis-brain-interface.kicad_pcb]
2023-11-20 PCB version 0.1.0.
    [anolis-brain-interface.kicad_pcb, anolis-brain-interface.kicad_sch]
2023-11-20 Order number corrected.
    [anolis-brain-interface.kicad_pcb, anolis-brain-interface.kicad_sch]
2023-11-20 Fixed inconsistent routing.
    [anolis-brain-interface.kicad_pcb]
2023-11-28 Replaced incorrect order number.
    [anolis-brain-interface.kicad_pcb, anolis-brain-interface.kicad_sch]
2023-12-01 Better plots.
    [data.csv]
